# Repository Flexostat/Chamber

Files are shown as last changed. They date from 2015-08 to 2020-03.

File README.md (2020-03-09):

# Production files:
### Chamber_xxmm_tube.stl 
Print one of these per chamber.  
  - __24mm__: kimax centrifuge tube or other 24mm tubes.
  - __25mm__: pyrex vista tubes or other 25mm tubes.

### xxx_magnet_holder.stl
  - __fan__: The magnet holder for the computer fan stirrer (digikey part: _P12820-ND_)
  - __stepper__: The magnet holder for the stepper motor (MPN: ST-PM35-15-11C, sparkfun.com PN: ROB-10551)

### Parameters 
The designs here have been updated to build in openSCAD (http://www.openscad.org/).  The top of the design files contains all parameters, which you can adjust to compensate intricacies of your printer.  To adjust parameters:

  1) Open the source file (.scad) in openSCAD.
  2) Edit parameter of your choice (it's recommended that you only make small changes).
  3) Select Design->Render and wait for rendering to complete (may take several minutes).
  4) Select File->Export->Export as STL... and save the STL.  
  
  <br />This work is licensed under a <a rel="license" href="http://creativecommons.org/licenses/by/4.0/">Creative Commons Attribution 4.0 International License</a>.

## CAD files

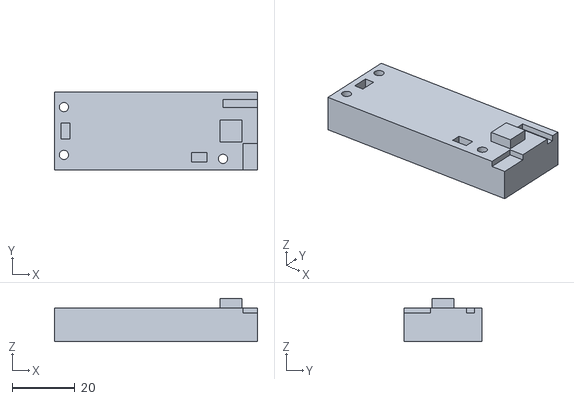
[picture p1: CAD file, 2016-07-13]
production_files/PCB_assembly_jig.stl
64.8 x 25.0 x 13.8

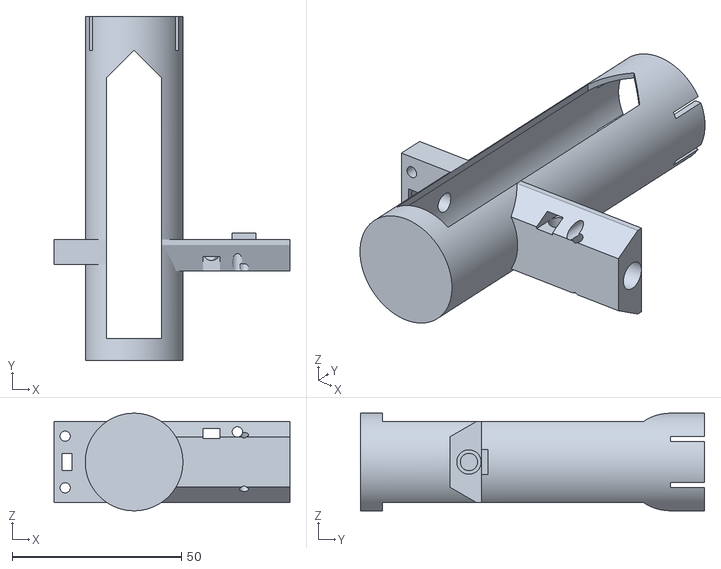
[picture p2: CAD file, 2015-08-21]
chamber_25mm_tube.stl
69.5 x 101.5 x 28.8

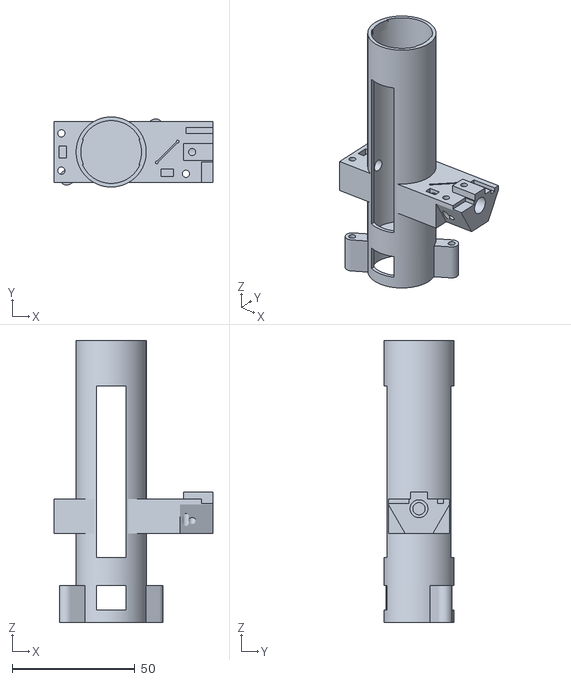
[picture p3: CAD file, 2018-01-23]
production_files/chamber_25mm_tube.stl
64.8 x 28.6 x 115.0

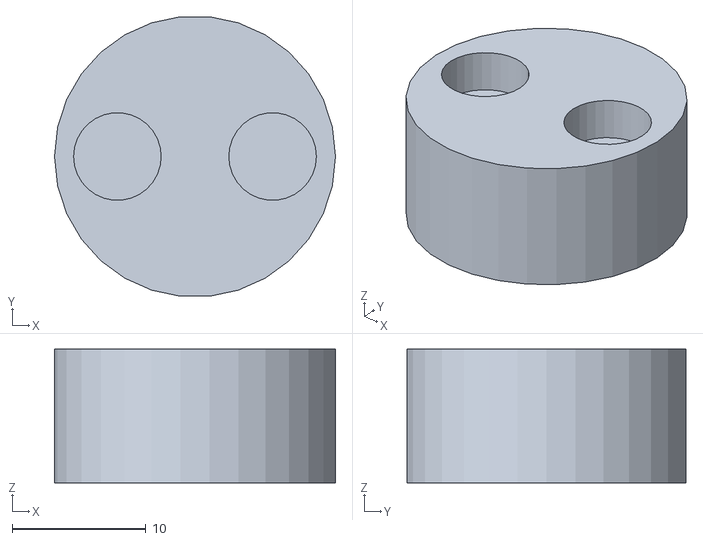
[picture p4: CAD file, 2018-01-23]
production_files/stepper_magnet_holder.stl
21.0 x 20.9 x 10.0

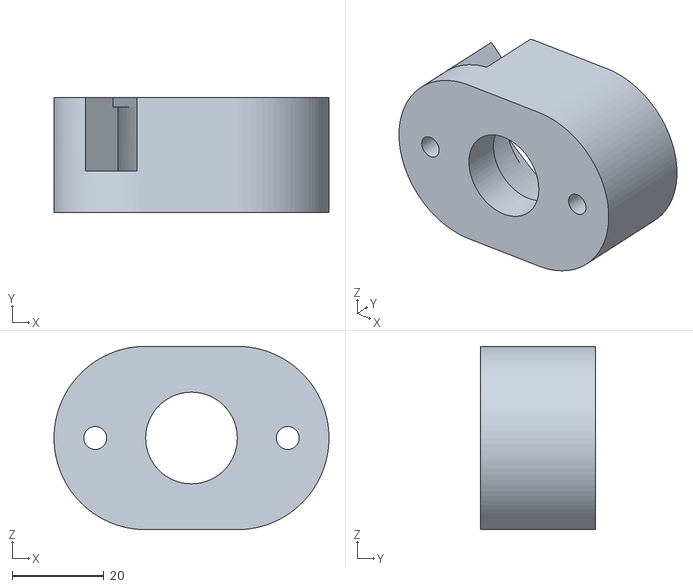
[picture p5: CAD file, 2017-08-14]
production_files/mortor_drill_jig.stl
60.0 x 25.0 x 40.0

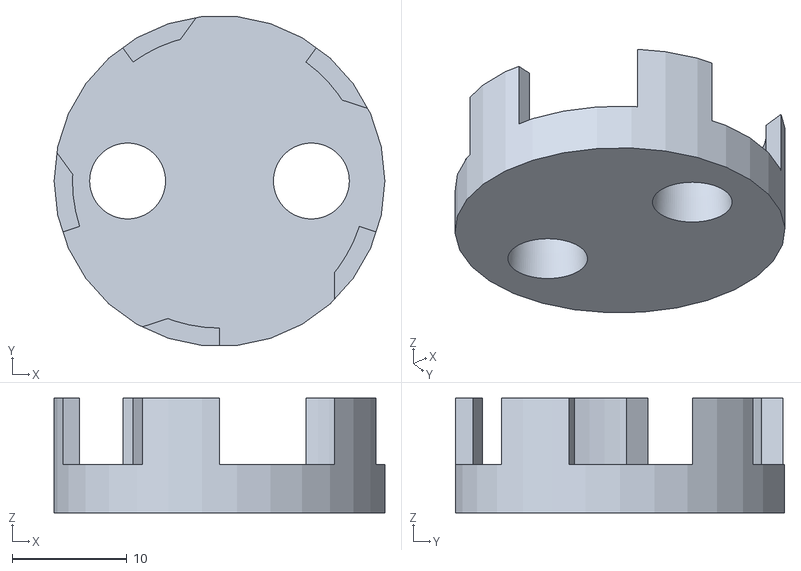
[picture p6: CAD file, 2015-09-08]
production_files/fan_magnet_holder.stl
28.8 x 28.6 x 10.0

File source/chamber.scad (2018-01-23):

//universal constants:
in = 25.4;

test = false;
//options:
heater_cut_size = 0; //0=off -- Experimental
fan_stir = 0; //0=stepper motor stir, 1=20mm fan stir

//general parameters
tap_hole_632 = 2.95;
splitter_size = 12; //12mmx12mm microscope slide
laser_length = 17;
laser_dia = 7.1; //7.1 for digikey laser.  6.1 for cheap chinese laser
laser_path_dia = 5;
laser_path_height = 30;
wall_thickness = 1.5;

//tube parameters
tube_diameter = 25.6; //chemglass 25mmx100mm //actual dia 24.7
//tube_diameter = 24.8; //kimax 24mm cfuge tube //actual diameter 23.8mm
tube_holder_wall = wall_thickness; 
tube_holder_height = 100;
tube_window_width = 12;
tab_depth = 1.75;

//PCB parameters.  These can't change without changing the PCB
sensor_holesize = [3,5];
sensor_depth = 3.8;
rx_llc = [-21.32,-2.5]; //lower left corner of RX sensor hole
tx_llc = [0.9*25.4-sensor_holesize[1]/2,-9.89]; //lower left corner of TX sensor hole
PCB_hole_locations = [[-20.32,7.62],[-20.32,-7.62],[1.2*25.4,-8.89]];
PCB_rect_holesize = [12,7];
PCB_rect_offset_out = 2.5;
PCB_rect_holecenter = [1.3*25.4,0];
PCB_height=25;
ethernet_ulc = [(2-0.55)*25.4,-3-1];
ethernet_size =[17,17];
ethernet_depth = 1.7;
header_ulc = [(2-0.8)*25.4,1.787*in/2-0.55*in-0.1/2*in];
PCB_tube_hole_diameter = 30; 
laser_end_x = 42.5;  
laser_zcomp = -0.1;

//Stir motor parameters
hole_dist = 42;
motor_mount_angle = 30;
//
fan_hole_dist = 32;
fan_hole_dia = 0.1495*25.4+.3; //clearance fit for 6-32
magnet_depth = fan_stir==1? 5.1+tube_holder_wall : 15; //fan depth : stepper depth

//derived parameters
splitter_center_x = abs(tx_llc[0])+sensor_holesize[1]/2;
base_depth = splitter_size-sensor_depth+2;
outer_diameter = min(PCB_tube_hole_diameter-1,tube_diameter+2*tube_holder_wall);
if(outer_diameter>PCB_tube_hole_diameter-1.01) {
  echo("WARNING: tube diameter parameter may be too large.");
}

/////////////////////////////////
//Assemble the whole part.     //
/////////////////////////////////
difference() {
  union() {
    tube_holder(tube_diameter);
    translate([0,0,laser_path_height+tube_holder_wall]) 
      PCB_and_optics();
    rotate([0,0,motor_mount_angle]) translate([0,0,-magnet_depth]) 
      stir_holder(magnet_depth,tube_diameter,hole_dist,window=false,fan=fan_stir); // do window later
  }
  //negative parts of tube holder and laser/pcb holder
  tube_holder_negative_parts(tube_diameter);
  translate([0,0,laser_path_height+tube_holder_wall]) 
    laser(tap_hole_632);

  //windows TODO: refactor into tube_holder_negative_parts
  translate([-tube_window_width/2,-50,tube_holder_wall+10]) 
    cube([tube_window_width,100,tube_holder_height*0.70], center=false);
  if(fan_stir==0){
    translate([-tube_window_width/2,-50,-10]) 
      cube([tube_window_width,100,10], center=false);
  }
  if (heater_cut_size>0) {
    translate([0,0,heater_cut_size/2])
    rect_helix(10,tube_holder_height,tube_diameter/2+heater_cut_size/2,heater_cut_size,300);
  }
  if (test) {
      cube([100,100,43],center=true);
      translate([0,0,115])
      cube([100,100,150],center=true);
      translate([-50,0,50])
      cube([100,100,100],center=true);
  }
}
if (!test){
    tube_tabs(tube_diameter);
}

/////////////////////////////////
//Modules                      //
/////////////////////////////////

module stir_holder(h,td,hole_offset,window=false,fan=0){
  $fn=100;
  if (fan==0) {
    difference() {
      union() {
        difference() {
          hull() {
            for(i = [hole_offset/2, -hole_offset/2]) {
              translate([i,0,0])
                cylinder(h=h,d=tap_hole_632+wall_thickness*2, center=false);
            } 
          }
          for(i = [hole_offset/2, -hole_offset/2]) {
            translate([i,0,0])
              cylinder(h=h,d=tap_hole_632, center=false);
          } 
        }
        cylinder(h=h, d=outer_diameter, center = false);
      }
      cylinder(h=h, d=td);
      if(window) {
        translate([-tube_window_width/2,-50,5]) 
          cube([tube_window_width,100,h-5], center=false);
      }
    }
  }
  else { //fan holder
    translate([0,0,tube_holder_wall])
    difference() {
      translate([-20,-20]) v_rounded_cube([40,40,h],4);
      for(x = [fan_hole_dist/2,-fan_hole_dist/2]) {
        for(y = [fan_hole_dist/2,-fan_hole_dist/2]) {
          translate([x,y,0])
            cylinder(h=2.1*h,d=fan_hole_dia , center=true,$fn=30);
          translate([x-10/2+2*x/abs(x),y-10/2+2*y/abs(y),h-2])
            v_rounded_cube([10,10,3],r=2);
        }
      }
      cylinder(h=(h-tube_holder_wall)*2 ,d=32,center=true);
    }
  }
}

module tube_holder(td) {
  $fn=200;
  //tube part
  cylinder(h=tube_holder_height, d=outer_diameter, center = false);
}

module tube_tabs(td) {
  $fn=100;
  //the tabs
  translate([0,0,tube_holder_height-5])
    intersection() {
      cube([100,10,10],center = true);
      difference() {
        cylinder(h=10,d=td+tube_holder_wall);
        //make cone 0.1 wider and taller to work around preview glitch
        translate([0,0,-0.1])cylinder(h=10+0.1,d1=td+0.1,d2=td-tab_depth);
      }
    }
}

module tube_holder_negative_parts(td) {
  $fn=200;
  //actual tube hole
  translate([0, 0, tube_holder_wall])
    cylinder(h=tube_holder_height, d=td);
  //tab cutouts
  //translate([-50,-1.5/2+5,tube_holder_height-10]) cube([100,1.5,10]);
  //translate([-50,-1.5/2-5,tube_holder_height-10]) cube([100,1.5,10]);
}

module PCB_and_optics() {
  difference() {
    PCB_body(rx_llc[0]-2,laser_end_x-1);
    PCB_holes(tap_hole_632);
    beam_splitter(splitter_size,0.6);
    laser(tap_hole_632);
    bevel(30+90,10,28,45);
    bevel(-30-90,10,28,45);
  }
}

module PCB_holes(screw_hole_dia) {
  $fn=200;
  linear_extrude(height=10,center = true ,convexity=10  )
  union() {
    translate(rx_llc)
      square(sensor_holesize,center=false);
    translate(tx_llc)
      square([sensor_holesize[1],sensor_holesize[0]],center=false);
  }
  linear_extrude(height=40,center = true ,convexity=10  )
    for (xy = PCB_hole_locations) {
      translate(xy)
        circle(d=screw_hole_dia);
    }
  translate([ethernet_ulc[0],
    ethernet_ulc[1]-ethernet_size[1],
    sensor_depth-ethernet_depth])
      cube([ethernet_size[0],ethernet_size[1],ethernet_depth+1],center = false);
  translate([header_ulc[0],header_ulc[1],sensor_depth-ethernet_depth])
    cube([0.8*25.4,0.1*25.4,2]);
}

module beam_splitter(size,thick) {
  color("blue")
  translate([0,0,-((size)/2)+sensor_depth-1/2])
    translate([splitter_center_x,0,0]) rotate([0,0,-45])
      union() {
        $fn = 10;
        cube([thick,size+1,size+1],center = true);
        translate([0,-(size)/2]) cylinder(h=size+1,d=2*thick,center = true);
        translate([0,(size)/2]) cylinder(h=size+1,d=2*thick,center = true);
      }

}

module laser(screw_hole_dia) {
  color("red") translate([rx_llc[0],0,laser_zcomp]) rotate([0,90,0]) 
  cylinder(h=abs(rx_llc[0])+splitter_center_x + splitter_size/sqrt(2)/2+1,
    d=laser_path_dia , center=false,$fn=30);
  color("red") translate([abs(tx_llc[0])+sensor_holesize[1]/2,0,laser_zcomp])
    rotate([90,0,0])
      cylinder(h=abs(tx_llc[1]),d=laser_path_dia , center=false,$fn=30);
  color("pink") translate([splitter_center_x + splitter_size/sqrt(2)/2+1,0,laser_zcomp])
    rotate([0,90,0])
      cylinder(h=laser_length,d=laser_dia+0.2,center=false,$fn=300);
  for (i = [0:360/3:359]) {
    rotate([i,0,0]) color("gray") translate([PCB_rect_holecenter[0],0,laser_zcomp]) 
      cylinder(h=20,d=screw_hole_dia,center=false,$fn=30);
  }
}
module bevel(angle,r,x1,x2) {
  rotate([angle,0,0]) translate([x1,-10,r])
    cube([abs(x2-x1),20,20],center = false);
}

module PCB_body(x1,x2) { //length of x in each dir 
  translate([x1,-PCB_height/2,-base_depth])
    cube([abs(x2-x1),PCB_height,sensor_depth+base_depth]);
  color("green") translate([PCB_rect_holecenter[0]-PCB_rect_holesize[0]/2+PCB_rect_offset_out
    ,PCB_rect_holecenter[1]-PCB_rect_holesize[1]/2,sensor_depth])
      cube([PCB_rect_holesize[0],PCB_rect_holesize[1],3],center = false);
}

module rect_helix(turns,height,r,cutsize,slices=100) {
  theta = atan((height/turns)/(PI*2*r));
  intersection() {
    for (i = [1:slices]) {
      hull() {
        rotate([0,0,turns/slices*360*i])
        translate([0,r,height/slices*i])
        rotate([0,theta,0])
        cube(cutsize,center=true);

        rotate([0,0,turns/slices*360*(i-1)])
        translate([0,r,height/slices*(i-1)])
        rotate([0,theta,0])
        cube(cutsize,center=true);
      }
    }
    cylinder(h=height,r=r*2);
  }
}


module v_rounded_cube(xyz,r,$fn=30) {
  z = xyz[2];
  y = xyz[1];
  x = xyz[0];
  translate([r,r])
  hull() {
    cylinder(h=z,r=r);
    translate([0,y-2*r])
    cylinder(h=z,r=r);
    translate([x-2*r,0])
    cylinder(h=z,r=r);
    translate([x-2*r,y-2*r])
    cylinder(h=z,r=r);
  }
}

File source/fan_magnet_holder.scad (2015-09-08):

thickness =1.6;
diameter = 25.2+0.4;
magnet_hole_dia = 6.6;
magnet_hole_depth = 4.2;
top_height = 4.2;
overall_height = 10;
hole_offset = 16/2;

translate([0, 0, overall_height]) rotate([180, 0, 0])
difference() {
  cylinder(h=overall_height,d=diameter+2*thickness);
  cylinder(h=(overall_height-top_height)*2, d=diameter, center=true,$fn=60);
  for (i = [hole_offset,-hole_offset]) {
    translate([i,0,overall_height-magnet_hole_depth]) 
      cylinder(h=magnet_hole_depth*2,d=magnet_hole_dia,center=true,$fn=100);
    translate([i,0,overall_height-0.3]) 
      cylinder(h=magnet_hole_depth,d2=magnet_hole_dia+0.6,d1=magnet_hole_dia,center=true,$fn=100);
  }
  for (i=[0:4]) {
  	rotate([0,0,360/5*i])
  	cube([10,100,(overall_height-top_height)]);
  }
}

//"tool" for pressing magnets
//translate([30,0])
	//cylinder(h=7,d=diameter-1);

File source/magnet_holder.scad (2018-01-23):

diameter = 21;
//magnet_hole_dia = 6.4;
magnet_hole_dia = 6.55;
//magnet_hole_depth = 4;
magnet_hole_depth = 3.2;
height = 10;
//shaft_dia = 3.05;
shaft_dia = 3.3;
shaft_depth = 8;
hole_offset = 5.8;


difference() {
  cylinder(h=height,d=diameter);
  for (i = [hole_offset,-hole_offset]) {
    translate([i,0,height]) 
      cylinder(h=magnet_hole_depth*2,d=magnet_hole_dia,center=true,$fn=30);
  }
  cylinder(h=2*shaft_depth, d=shaft_dia, center=true,$fn=30);
  #cylinder(h=2 ,d2=shaft_dia,d1=shaft_dia+0.8,,center=true,$fn=30);
}

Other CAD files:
source/PCB_assembly_jig.scad
source/motor drill jig.f3d

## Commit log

2013-08-05 updated chamber. raised laser height to avoid catching stirbar. reworked laser holder, should be a lot more accurate and secure. version number 7.
2013-08-06 added stl files
    [chamber.stl, magnet holder.stl, motor mount.stl]
2014-01-11 tweaked file names to remove spaces
    [magnet_holder.stl, motor_mount.stl]
2014-01-11 added step and stl versions of all 3d parts
    also added different sized pinch valves clips.
    [chamber.stl, chamber.stp, magnet_holder.stl, magnet_holder.stp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]
2014-04-04 updated chamber design to accomidate the new motor
    [magnet_holder.stl, magnet_holder.stp, motor_mount.stl, motor_mount.stp]
2014-05-13 reorg directory structure
    [chamber.stp, magnet_holder.stp, motor_mount.stp]
2014-11-18 added a full chamber assembly for printing on SLS printers
    [Chamber_full_assembly.stl]
2015-04-14 minor chamber update
    [chamber.stl]
2015-08-21 experimental new designs
    [chamber_25mm_tube.stl]
2015-08-22 switched to openSCAD. These designs should work!
    [Chamber_full_assembly.stl, chamber.scad, chamber.stl, chamber.stp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]
2015-08-29 working for 25mm tubes, printing at .3mm layers
    [chamber.scad, chamber_25mm_tube_fan_mount.stl]
2015-08-30 holes go all the way through
    [chamber.scad]
2015-09-08 magnet holder
    [fan_magnet_holder.scad]
2015-09-08 soldering jig
    [PCB_assembly_jig.scad, fan_magnet_holder.stl]
2015-09-24 parameter updates (working)
    [chamber.scad]
2015-09-24 recessed screws
    [chamber.scad]
2015-09-30 update stls
    [chamber_25mm_tube_fan_mount.stl]
2015-12-21 new prod file
    [chamber.scad, chamber_24mm_tube_fan_mount.stl]
2016-07-13 update for newer boards
    [PCB_assembly_jig.scad, PCB_assembly_jig.stl, chamber.scad, chamber_24mm_tube.stl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]
2017-07-17 small tweak to ease assembly
    [magnet_holder.scad, stepper_magnet_holder.stl]
2017-08-14 slight tweak to fit laser better
    [chamber_25mm_tube.stl]
2017-08-14 drill jig for motor
    [mortor_drill_jig.stl, motor drill jig.f3d]
2018-01-23 printability tweaks
    [magnet_holder.scad, stepper_magnet_holder.stl]
2018-01-23 changes to improve laser alignment with newest pcb
    [chamber.scad, chamber_25mm_tube.stl]
